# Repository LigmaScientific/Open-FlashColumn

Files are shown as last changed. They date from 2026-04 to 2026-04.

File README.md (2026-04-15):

# Open-FlashColumn
An open-source flash-column chromatography system.

Abstract

Flash column chromatography is a method used in organic synthesis research to separate and purify chemicals. Compounds are separated by being forced through silica gel with a pressurized solvent, which separates them based on polarity. The project focuses on the research and development of a flash-column chromatography column that enables users to visualize the separation of compounds in real-time using an ultraviolet lamp and fluorescent silica. The system was constructed using a combination of 3D-printed components and commercial off-the-shelf components to minimize costs. Furthermore, the apparatus is designed for easy visualization of fractions, needing only a handheld UV lamp at 254nm to visualize the absorbance of each analyte as they separate. The 3D-printed components are designed to be durable against both chemicals and UV radiation, and can be manufactured on commonly available printers using standard filaments. The flash column can resolve a wide range of analytes and works with mixtures of ethyl acetate and hexane. Separations are on par with or more efficient than traditional flash columns, and the system offers ease of use that falls somewhere between commercial flash chromatography machines and traditional flash columns. The low per-unit cost and commercial-off-the-shelf components make the system both affordable and accessible, making it well-suited for use in teaching laboratories and those on a tight budget. The project is intended to be open-source, with digital files published under a permissive license that allows others to reproduce the results and build upon the column. This ensures continued support for the project so that the system will be easily repairable.

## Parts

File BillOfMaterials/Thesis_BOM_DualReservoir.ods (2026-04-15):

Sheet: 2-Reservoir-DIY
Component | Size | QTY (build) | QTY (purchase) | Unit Price | Total Price | SKU | Link | Manufacturer | Source | Notes
SwageLok MNPT-Tube fitting | 1/8” MNPT x 1/8” tube | 9 | 9 | $5.50 | $49.50 | B-200-1-2 | https://products.swagelok.com/en/c/straights/p/B-200-1-2 | Swagelok | W&M Chem Dept. | Comes w/ Nuts and Ferrules
SwageLok Nut | 1/8” tube | 0 | 10 | $1.56 | $15.60 | B-202-1 | https://products.swagelok.com/en/c/female-nuts/p/B-202-1 | Swagelok | W&M Chem Dept. | Spares
Swagelok ferrule | 1/8” tube | 0 | 10 | $1.70 | $17.00 | B-200-SET | https://products.swagelok.com/en/c/ferrule-sets/p/B-200-SET | Swagelok | W&M Chem Dept. | Spares
Swagelok bulkhead fitting | 1/8” tube | 2 | 2 | $16.83 | $33.66 | B-200-61 | https://products.swagelok.com/en/c/straights/p/B-200-61 | Swagelok | W&M Chem Dept. | Can be substituted w/ thru-bore swagelok fitting, however tubing length for reservoir is fixed if done so
FNPT-MNPT standoff | 1/8” FNPT x 1/8” MNPT | 4 | 1 | $9.99 | $9.99 | 769018946082 | https://www.amazon.com/JSMOUID-Adapters-Extension-Connectors-Bathroom/dp/B0DXCZHD25 | JSMOUID | Amazon | 4-pack
3/8” Brass Washer | 3/8 ID, ½ OD | 2 | 2 | $0.75 | $1.50 | 1297-P |  | Hillman | ACE hardware
1/8” OD, 1/16” ID Copper tubing | 1.5” long | 1 | 1 | $6.89 | $6.89 | B07QVND41W | https://www.amazon.com/uxcell-Refrigeration-Tubing-inches-Copper/dp/B07QZVLB82/ | Restek | W&M Chem Dept. | generic tubing linked
1/8” OD, 1/16” ID PTFE tubing | 20.5” long | 1 | 1 | $20.80 | $20.80 | 193005153809 | https://www.amazon.com/dp/B07K7RRW93 | USA Sealing Inc | Amazon | 1 pack covers all the tubing, arbitrary length (for convenience); 10 feet total
1/8” OD, 1/16” ID PTFE tubing | 16” long | 2 |  |  | $0.00
1/8” OD, 1/16” ID PTFE tubing | 10.5” long | 2 |  |  | $0.00
1/8” OD, 1/16” ID PTFE tubing | 9.5” long | 2 |  |  | $0.00 |  |  |  |  | Reservoir tube, must be exact
¼” silicone tube | 36” long | 2 | 1 | $8.69 | $8.69 | B0DST875BW | https://www.amazon.com/Rebower-Silicone-Silicon-Brewing-Aquarium/dp/B0DST875BW | Rebower | Amazon | 1 pack covers all the tubing, arbitrary length (for convenience); 10 feet total
¼” silicone tube | 24” long | 1 |  |  | $0.00 |  |  |  |  | Arbitrary length
¼” tube tee-joint | ¼” tube | 1 | 1 | $4.99 | $4.99 | QL2406371TA008K1 | https://www.amazon.com/PAGOW-Fitting-Plastic-Barbed-Household/dp/B0DNYX6LYN | PAGOW | Amazon | 4-pack, only need one
Pressure gauge, 30 PSI | 1/8” MNPT | 2 | 2 | $14.15 | $28.30 | 4000K717 | https://www.mcmaster.com/4000K717/ | Ashcroft | Mcmaster
Pressure relief valve, 25 PSI | 1/8” MNPT | 2 | 2 | $11.45 | $22.90 | SRH250-18 | https://www.amazon.com/dp/B0B32RQDM5 | Conrader | Amazon | Can be substituted w/ McMaster 4772K2
Ball valve, NPT | 1/8” FNPT x 1/8” MNPT | 2 | 2 | $18.99 | $37.98 | 1zf-00425-mvn | https://www.amazon.com/dp/B0D2MTSMMZ | Beduan | Amazon | 3 used, though a fourth can be used to increase deadspace for analyte loading.
NPT tee | FNPT x 1/8” FNPT x 1/8” MNPT | 2 | 1 | $6.99 | $6.99 | SG-PFBST18-2_1 | https://www.amazon.com/dp/B0B9M4HKMT | SUNGATOR | Amazon | 2-Pack
¼” barb fitting | 1/8” MNPT | 2 | 1 | $6.99 | $6.99 | CA-125 4A-4 | https://www.amazon.com/dp/B07P962KXQ | KOOTANS | Amazon | 4-pack, only need two
Precision needle valve | 1/8” FNPT x 1/8” FNPT | 2 | 2 | $52.71 | $105.42 | 46425K11 | https://www.mcmaster.com/46425K11/ | Deltrol | McMaster | valve is directional
Viton O-ring | -123 | 2 | 1 | $9.64 | $9.64 | 9464K87 | https://www.mcmaster.com/9464K87/ |  | McMaster | 25-pack
Buna-N Gasket | 2-1/2” nominal | 2 | 2 | $2.54 | $5.08 | 4524K51 | https://www.mcmaster.com/4524K51/ |  | McMaster
Neoprene gasket | 5/16” ID, ¾” OD, 1/16” thick | 2 | 2 | $0.65 | $1.30 | 3183-D |  | Hillman | ACE hardware | can be substituted w/ buna-n or viton if needed.
Brass Bulkhead nut | 3/8-24, incl. w/ bulkhead | 2 | 0 |  | $0.00 |  |  | Hillman | W&M Chem Dept. | Included w/ bulkhead
10-32 threaded rod | 9.5” long | 2 | 1 | $2.39 | $2.39 | 98838A011 | https://www.mcmaster.com/products/98838a011/ |  | McMaster | 3’, Cut to match length of column
10-32 wing nuts | 10-32 thread | 2 | 2 | $0.69 | $1.38 | 4341-D |  | Hillman | ACE hardware
#10 washers | 10 | 4 | 4 | $0.15 | $0.60 | 8305556 |  | Hillman | ACE hardware
10-32 acorn nuts | 10-32 thread | 2 | 2 | $0.99 | $1.98 | 861-R |  | Hillman | ACE hardware | Use Blue thread; brass, can be galvanized
GL-80 bottle | GL-80 thread | 2 | 1 | $35.99 | $35.99 | 611851182250 | https://www.amazon.com/dp/B0912N5WJT | Moonetto | Amazon | 3-pack
GL-80 lid, PETG | GL-80 thread | 2 | 2 | 62.03g | 124.06g | N/A |  | DIY | DIY | 3D printed
4-port lid, PETG | 1/8” NPT (tapped), 7mm hole (bulkhead) | 2 | 2 | 37.36g | 74.72g | N/A |  | DIY | DIY | 3D printed, Solvent Sealed
PETG Endcap (Top) | 1/8” FNPT | 1 | 1 | 78.22g | 78.22g | N/A |  | DIY | DIY | 3D printed, Solvent Sealed
PETG Endcap (Bottom) | 1/8” FNPT | 1 | 1 | 75.58g | 75.58g | N/A |  | DIY | DIY | 3D printed, Solvent Sealed
PETG Mixer | 1/8” FNPT | 1 | 1 | 28.71g | 28.71g | N/A |  | DIY | DIY | 3D printed, Solvent Sealed
PETG Peak Tracker | 30.45mm ID | 1 | 1 | 8.52g | 8.52g | N/A |  | DIY | DIY | 3D printed
PETG Locking Ring | 30.45mm ID | 2 | 2 | 10.15g | 20.30g | N/A |  | DIY | DIY | 3D printed
Quartz Envelope | 200mm length, 30 mm OD, 2.5 mm wall thickness | 1 | 1 | $20.00 | $20.00 | ‎B0C2875X67 | https://www.amazon.com/dp/B0C2875X67 | Deschem Scientific Supply | Amazon | Can be substituted w/ borosilicate glass if external detector is used. Can be longer.
Polymaker PETG | 1 kg | 1 | 1 | $18.99 | $18.99 | B0FG3FHG29 | https://www.amazon.com/dp/B0FG3FHG29 | Polymaker | Amazon
Aggregate price: | $474.55 |  |  |  |  |  |  |  | W&M means I got it from the Chem Department; can be ordered w/ an account

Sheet: 2-Reservoir-PrintPurchase
Component | Size | QTY (build) | QTY (purchase) | Unit Price | Total Price | SKU | Link | Manufacturer | W&M Chem Dept. | Notes
SwageLok MNPT-Tube fitting | 1/8” MNPT x 1/8” tube | 9 | 9 | $5.50 | $49.50 | B-200-1-2 | https://products.swagelok.com/en/c/straights/p/B-200-1-2 | Swagelok | W&M Chem Dept. | Comes w/ Nuts and Ferrules
SwageLok Nut | 1/8” tube | 13 | 10 | $1.56 | $15.60 | B-202-1 | https://products.swagelok.com/en/c/female-nuts/p/B-202-1 | Swagelok | W&M Chem Dept. | Spares
Swagelok ferrule | 1/8” tube | 13 | 10 | $1.70 | $17.00 | B-200-SET | https://products.swagelok.com/en/c/ferrule-sets/p/B-200-SET | Swagelok | W&M Chem Dept. | Spares
Swagelok bulkhead fitting | 1/8” tube | 2 | 2 | $16.83 | $33.66 | B-200-61 | https://products.swagelok.com/en/c/straights/p/B-200-61 | Swagelok | W&M Chem Dept. | Can be substituted w/ thru-bore swagelok fitting, however tubing length for reservoir is fixed if done so
FNPT-MNPT standoff | 1/8” FNPT x 1/8” MNPT | 4 | 1 | $9.99 | $9.99 | 769018946082 | https://www.amazon.com/JSMOUID-Adapters-Extension-Connectors-Bathroom/dp/B0DXCZHD25 | JSMOUID | Amazon | 4-pack
3/8” Brass Washer | 3/8 ID, ½ OD | 2 | 2 | $0.75 | $1.50 | 1297-P |  | Hillman | ACE hardware
1/8” OD, 1/16” ID Copper tubing | 1.5” long | 1 | 1 | $6.89 | $6.89 | B07QVND41W | https://www.amazon.com/uxcell-Refrigeration-Tubing-inches-Copper/dp/B07QZVLB82/ | Restek | W&M Chem Dept. | generic tubing linked
1/8” OD, 1/16” ID PTFE tubing | 20.5” long | 1 | 1 | $20.80 | $20.80 | 193005153809 | https://www.amazon.com/dp/B07K7RRW93 | USA Sealing Inc | Amazon | 1 pack covers all the tubing, arbitrary length (for convenience); 10 feet total
1/8” OD, 1/16” ID PTFE tubing | 16” long | 2 |  |  | $0.00
1/8” OD, 1/16” ID PTFE tubing | 10.5” long | 2 |  |  | $0.00
1/8” OD, 1/16” ID PTFE tubing | 9.5” long | 2 |  |  | $0.00 |  |  |  |  | Reservoir tube, must be exact
¼” silicone tube | 36” long | 2 | 1 | $8.69 | $8.69 | B0DST875BW | https://www.amazon.com/Rebower-Silicone-Silicon-Brewing-Aquarium/dp/B0DST875BW | Rebower | Amazon | 1 pack covers all the tubing, arbitrary length (for convenience); 10 feet total
¼” silicone tube | 24” long | 1 |  |  | $0.00 |  |  |  |  | Arbitrary length
¼” tube tee-joint | ¼” tube | 1 | 1 | $4.99 | $4.99 | QL2406371TA008K1 | https://www.amazon.com/PAGOW-Fitting-Plastic-Barbed-Household/dp/B0DNYX6LYN | PAGOW | Amazon | 4-pack, only need one
Pressure gauge, 30 PSI | 1/8” MNPT | 2 | 2 | $14.15 | $28.30 | 4000K717 | https://www.mcmaster.com/4000K717/ | Ashcroft | Mcmaster
Pressure relief valve, 25 PSI | 1/8” MNPT | 2 | 2 | $11.45 | $22.90 | SRH250-18 | https://www.amazon.com/dp/B0B32RQDM5 | Conrader | Amazon | Can be substituted w/ McMaster 4772K2
Ball valve, NPT | 1/8” FNPT x 1/8” MNPT | 2 | 2 | $18.99 | $37.98 | 1zf-00425-mvn | https://www.amazon.com/dp/B0D2MTSMMZ | Beduan | Amazon | 3 used, though a fourth can be used to increase deadspace for analyte loading.
NPT tee | FNPT x 1/8” FNPT x 1/8” MNPT | 2 | 1 | $6.99 | $6.99 | SG-PFBST18-2_1 | https://www.amazon.com/dp/B0B9M4HKMT | SUNGATOR | Amazon | 2-Pack
¼” barb fitting | 1/8” MNPT | 2 | 1 | $6.99 | $6.99 | CA-125 4A-4 | https://www.amazon.com/dp/B07P962KXQ | KOOTANS | Amazon | 4-pack, only need two
Precision needle valve | 1/8” FNPT x 1/8” FNPT | 2 | 2 | $52.71 | $105.42 | 46425K11 | https://www.mcmaster.com/46425K11/ | Deltrol | McMaster | valve is directional
Viton O-ring | -123 | 2 | 1 | $9.64 | $9.64 | 9464K87 | https://www.mcmaster.com/9464K87/ |  | McMaster | 25-pack
Buna-N Gasket | 2-1/2” nominal | 2 | 2 | $2.54 | $5.08 | 4524K51 | https://www.mcmaster.com/4524K51/ |  | McMaster
Neoprene gasket | 5/16” ID, ¾” OD, 1/16” thick | 2 | 2 | $0.65 | $1.30 | 3183-D |  | Hillman | ACE hardware | can be substituted w/ buna-n or viton if needed.
Brass Bulkhead nut | 3/8-24, incl. w/ bulkhead | 2 | 0 |  | $0.00 |  |  | Hillman | W&M Chem Dept. | Included w/ bulkhead
10-32 threaded rod | 9.5” long | 2 | 1 | $2.39 | $2.39 | 98838A011 | https://www.mcmaster.com/products/98838a011/ |  | McMaster | 3’, Cut to match length of column
10-32 wing nuts | 10-32 thread | 2 | 2 | $0.69 | $1.38 | 4341-D |  | Hillman | ACE hardware
#10 washers | 10 | 4 | 4 | $0.15 | $0.60 | 8305556 |  | Hillman | ACE hardware
10-32 acorn nuts | 10-32 thread | 2 | 2 | $0.99 | $1.98 | 861-R |  | Hillman | ACE hardware | Use Blue thread; brass, can be galvanized
GL-80 bottle | GL-80 thread | 2 | 1 | $35.99 | $35.99 | 611851182250 | https://www.amazon.com/dp/B0912N5WJT | Moonetto | Amazon | 3-pack
GL-80 lid, PETG | GL-80 thread | 2 | 2 | $10.70 | $21.40 | N/A |  | Ligma Scientific | Ligma Scientific | For Print Purchase, prices may vary from vendor to vendor. Ligma Scientific charges $0.05/g plus $1.00 per print hour.
4-port lid, PETG | 1/8” NPT (tapped), 7mm hole (bulkhead) | 2 | 2 | $5.49 | $10.98 | N/A |  | Ligma Scientific | Ligma Scientific
PETG Endcap (Top) | 1/8” FNPT | 1 | 1 | $10.56 | $10.56 | N/A |  | Ligma Scientific | Ligma Scientific
PETG Endcap (Bottom) | 1/8” FNPT | 1 | 1 | $11.32 | $11.32 | N/A |  | Ligma Scientific | Ligma Scientific
PETG Mixer | 1/8” FNPT | 1 | 1 | $6.63 | $6.63 | N/A |  | Ligma Scientific | Ligma Scientific
PETG Peak Tracker | 30.45mm ID | 1 | 1 | $1.61 | $1.61 |  |  | Ligma Scientific | Ligma Scientific
PETG Locking Ring | 30.45mm ID | 2 | 2 | $1.82 | $3.64 |  |  | Ligma Scientific | Ligma Scientific
Quartz Envelope | 200mm length, 30 mm OD, 2.5 mm wall thickness | 1 | 1 | $20.00 | $20.00 | ‎B0C2875X67 | https://www.amazon.com/dp/B0C2875X67 | Deschem Scientific Supply | Amazon | Can be substituted w/ borosilicate glass if external detector is used. Can be longer.
Aggregate price: | $521.70

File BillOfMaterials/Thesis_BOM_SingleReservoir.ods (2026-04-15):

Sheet: 1-Reservoir-DIY
Component | Size | QTY (build) | QTY (purchase) | Unit Price | Total Price | SKU | Link | Manufacturer | Source | Notes
SwageLok MNPT-Tube fitting | 1/8” MNPT x 1/8” tube | 6 | 6 | $5.50 | $33.00 | B-200-1-2 | https://products.swagelok.com/en/c/straights/p/B-200-1-2 | Swagelok | W&M Chem Dept. | Comes w/ Nuts and Ferrules
SwageLok Nut | 1/8” tube | 0 | 10 | $1.56 | $15.60 | B-202-1 | https://products.swagelok.com/en/c/female-nuts/p/B-202-1 | Swagelok | W&M Chem Dept. | Spares
Swagelok ferrule | 1/8” tube | 0 | 10 | $1.70 | $17.00 | B-200-SET | https://products.swagelok.com/en/c/ferrule-sets/p/B-200-SET | Swagelok | W&M Chem Dept. | Spares
Swagelok bulkhead fitting | 1/8” tube | 1 | 1 | $16.83 | $16.83 | B-200-61 | https://products.swagelok.com/en/c/straights/p/B-200-61 | Swagelok | W&M Chem Dept. | Can be substituted w/ thru-bore swagelok fitting, however tubing length for reservoir is fixed if done so
FNPT-MNPT standoff | 1/8” FNPT x 1/8” MNPT | 2 | 1 | $9.99 | $9.99 | 769018946082 | https://www.amazon.com/JSMOUID-Adapters-Extension-Connectors-Bathroom/dp/B0DXCZHD25 | JSMOUID | Amazon | 4-pack
3/8” Brass Washer | 3/8 ID, ½ OD | 1 | 1 | $0.75 | $0.75 | 1297-P |  | Hillman | ACE hardware
1/8” OD, 1/16” ID Copper tubing | 1.5” long | 1 | 1 | $6.89 | $6.89 | B07QVND41W | https://www.amazon.com/uxcell-Refrigeration-Tubing-inches-Copper/dp/B07QZVLB82/ | Restek | W&M Chem Dept. | generic tubing linked
1/8” OD, 1/16” ID PTFE tubing | 20.5” long | 1 | 1 | $20.80 | $20.80 | 193005153809 | https://www.amazon.com/dp/B07K7RRW93 | USA Sealing Inc | Amazon | 1 pack covers all the tubing, arbitrary length (for convenience); 10 feet total
1/8” OD, 1/16” ID PTFE tubing | 16” long | 0 |  |  | $0.00
1/8” OD, 1/16” ID PTFE tubing | 10.5” long | 0 |  |  | $0.00
1/8” OD, 1/16” ID PTFE tubing | 9.5” long | 1 |  |  | $0.00 |  |  |  |  | Reservoir tube, must be exact
¼” silicone tube | 36” long | 1 | 1 | $8.69 | $8.69 | B0DST875BW | https://www.amazon.com/Rebower-Silicone-Silicon-Brewing-Aquarium/dp/B0DST875BW | Rebower | Amazon | 1 pack covers all the tubing, arbitrary length (for convenience); 10 feet total
¼” silicone tube | 24” long | 0 |  |  | $0.00 |  |  |  |  | Arbitrary length
¼” tube tee-joint | ¼” tube | 1 | 1 | $4.99 | $4.99 | QL2406371TA008K1 | https://www.amazon.com/PAGOW-Fitting-Plastic-Barbed-Household/dp/B0DNYX6LYN | PAGOW | Amazon | 4-pack, only need one
Pressure gauge, 30 PSI | 1/8” MNPT | 1 | 1 | $14.15 | $14.15 | 4000K717 | https://www.mcmaster.com/4000K717/ | Ashcroft | Mcmaster
Pressure relief valve, 25 PSI | 1/8” MNPT | 1 | 1 | $11.45 | $11.45 | SRH250-18 | https://www.amazon.com/dp/B0B32RQDM5 | Conrader | Amazon | Can be substituted w/ McMaster 4772K2
Ball valve, NPT | 1/8” FNPT x 1/8” MNPT | 2 | 1 | $18.99 | $18.99 | 1zf-00425-mvn | https://www.amazon.com/dp/B0D2MTSMMZ | Beduan | Amazon | 2 used, though a third can be used to increase deadspace for analyte loading.
 |  |  |  |  | $0.00
NPT tee | FNPT x 1/8” FNPT x 1/8” MNPT | 2 | 1 | $6.99 | $6.99 | SG-PFBST18-2_1 | https://www.amazon.com/dp/B0B9M4HKMT | SUNGATOR | Amazon | 2-Pack
¼” barb fitting | 1/8” MNPT | 1 | 1 | $6.99 | $6.99 | CA-125 4A-4 | https://www.amazon.com/dp/B07P962KXQ | KOOTANS | Amazon | 4-pack, only need two
Precision needle valve | 1/8” FNPT x 1/8” FNPT | 1 | 1 | $52.71 | $52.71 | 46425K11 | https://www.mcmaster.com/46425K11/ | Deltrol | McMaster | valve is directional
Viton O-ring | -123 | 1 | 1 | $9.64 | $9.64 | 9464K87 | https://www.mcmaster.com/9464K87/ |  | McMaster | 25-pack
Buna-N Gasket | 2-1/2” nominal | 1 | 1 | $2.54 | $2.54 | 4524K51 | https://www.mcmaster.com/4524K51/ |  | McMaster
 |  |  |  |  | $0.00
Neoprene gasket | 5/16” ID, ¾” OD, 1/16” thick | 1 | 1 | $0.65 | $0.65 | 3183-D |  | Hillman | ACE hardware | can be substituted w/ buna-n or viton if needed.
Brass Bulkhead nut | 3/8-24, incl. w/ bulkhead | 1 | 0 |  | $0.00 |  |  | Hillman | W&M Chem Dept. | Included w/ bulkhead
10-32 threaded rod | 9.5” long | 2 | 1 | $2.39 | $2.39 | 98838A011 | https://www.mcmaster.com/products/98838a011/ |  | McMaster | 3’, Cut to match length of column
10-32 wing nuts | 10-32 thread | 2 | 2 | $0.69 | $1.38 | 4341-D |  | Hillman | ACE hardware
#10 washers | 10 | 4 | 4 | $0.15 | $0.60 | 8305556 |  | Hillman | ACE hardware
10-32 acorn nuts | 10-32 thread | 2 | 2 | $0.99 | $1.98 | 861-R |  | Hillman | ACE hardware | Use Blue thread; brass, can be galvanized
GL-80 bottle | GL-80 thread | 2 | 1 | $35.99 | $35.99 | 611851182250 | https://www.amazon.com/dp/B0912N5WJT | Moonetto | Amazon | 3-pack
GL-80 lid, PETG | GL-80 thread | 1 | 1 | 62.03g | 62.03g | N/A |  | Ligma Scientific | Ligma Scientific | 3D printed
4-port lid, PETG | 1/8” NPT (tapped), 7mm hole (bulkhead) | 1 | 1 | 37.36g | 37.36g | N/A |  | Ligma Scientific | Ligma Scientific | 3D printed, Solvent Sealed
PETG Endcap (Top) | 1/8” FNPT | 1 | 1 | 78.22g | 78.22g | N/A |  | Ligma Scientific | Ligma Scientific | 3D printed, Solvent Sealed
PETG Endcap (Bottom) | 1/8” FNPT | 1 | 1 | 75.58g | 75.58g | N/A |  | Ligma Scientific | Ligma Scientific | 3D printed, Solvent Sealed
PETG Peak Tracker | 30.45mm ID | 1 | 1 | 8.52g | 8.52g | N/A |  | Ligma Scientific | Ligma Scientific | 3D printed
PETG Locking Ring | 30.45mm ID | 2 | 2 | 10.15g | 10.15g | N/A |  | Ligma Scientific | Ligma Scientific | 3D printed
Quartz Envelope | 200mm length, 30 mm OD, 2.5 mm wall thickness | 1 | 1 | $20.00 | $20.00 | ‎B0C2875X67 | https://www.amazon.com/dp/B0C2875X67 | Deschem Scientific Supply | Amazon | Can be substituted w/ borosilicate glass if external detector is used. Can be longer.
Polymaker PETG | 1 kg | 1 | 1 | $18.99 | $18.99 | B0FG3FHG29 | https://www.amazon.com/dp/B0FG3FHG29 | Polymaker | Amazon | only purchase if printing
Aggregate price: | $339.98 |  |  |  |  |  |  |  | W&M means I got it from the Chem Department; can be ordered w/ an account

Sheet: 1-Reservoir-PrintPurchase
Component | Size | QTY (build) | QTY (purchase) | Unit Price | Total Price | SKU | Link | Manufacturer | Source | Notes
SwageLok MNPT-Tube fitting | 1/8” MNPT x 1/8” tube | 6 | 6 | $5.50 | $33.00 | B-200-1-2 | https://products.swagelok.com/en/c/straights/p/B-200-1-2 | Swagelok | W&M Chem Dept. | Comes w/ Nuts and Ferrules
SwageLok Nut | 1/8” tube | 13 | 10 | $1.56 | $20.28 | B-202-1 | https://products.swagelok.com/en/c/female-nuts/p/B-202-1 | Swagelok | W&M Chem Dept. | Spares
Swagelok ferrule | 1/8” tube | 13 | 10 | $1.70 | $22.10 | B-200-SET | https://products.swagelok.com/en/c/ferrule-sets/p/B-200-SET | Swagelok | W&M Chem Dept. | Spares
Swagelok bulkhead fitting | 1/8” tube | 1 | 1 | $16.83 | $16.83 | B-200-61 | https://products.swagelok.com/en/c/straights/p/B-200-61 | Swagelok | W&M Chem Dept. | Can be substituted w/ thru-bore swagelok fitting, however tubing length for reservoir is fixed if done so
FNPT-MNPT standoff | 1/8” FNPT x 1/8” MNPT | 2 | 1 | $9.99 | $9.99 | 769018946082 | https://www.amazon.com/JSMOUID-Adapters-Extension-Connectors-Bathroom/dp/B0DXCZHD25 | JSMOUID | Amazon | 4-pack
3/8” Brass Washer | 3/8 ID, ½ OD | 1 | 1 | $0.75 | $0.75 | 1297-P |  | Hillman | ACE hardware
1/8” OD, 1/16” ID Copper tubing | 1.5” long | 1 | 1 | $6.89 | $6.89 | B07QVND41W | https://www.amazon.com/uxcell-Refrigeration-Tubing-inches-Copper/dp/B07QZVLB82/ | Restek | W&M Chem Dept. | generic tubing linked
1/8” OD, 1/16” ID PTFE tubing | 20.5” long | 1 | 1 | $20.80 | $20.80 | 193005153809 | https://www.amazon.com/dp/B07K7RRW93 | USA Sealing Inc | Amazon | 1 pack covers all the tubing, arbitrary length (for convenience); 10 feet total
1/8” OD, 1/16” ID PTFE tubing | 16” long | 0
1/8” OD, 1/16” ID PTFE tubing | 10.5” long | 0
1/8” OD, 1/16” ID PTFE tubing | 9.5” long | 1 |  |  |  |  |  |  |  | Reservoir tube, must be exact
¼” silicone tube | 36” long | 1 | 1 | $8.69 | $8.69 | B0DST875BW | https://www.amazon.com/Rebower-Silicone-Silicon-Brewing-Aquarium/dp/B0DST875BW | Rebower | Amazon | 1 pack covers all the tubing, arbitrary length (for convenience); 10 feet total
¼” silicone tube | 24” long | 0 |  |  |  |  |  |  |  | Arbitrary length
¼” tube tee-joint | ¼” tube | 1 | 1 | $4.99 | $4.99 | QL2406371TA008K1 | https://www.amazon.com/PAGOW-Fitting-Plastic-Barbed-Household/dp/B0DNYX6LYN | PAGOW | Amazon | 4-pack, only need one
Pressure gauge, 30 PSI | 1/8” MNPT | 1 | 1 | $14.15 | $14.15 | 4000K717 | https://www.mcmaster.com/4000K717/ | Ashcroft | Mcmaster
Pressure relief valve, 25 PSI | 1/8” MNPT | 1 | 1 | $11.45 | $11.45 | SRH250-18 | https://www.amazon.com/dp/B0B32RQDM5 | Conrader | Amazon | Can be substituted w/ McMaster 4772K2
Ball valve, NPT | 1/8” FNPT x 1/8” MNPT | 2 | 1 | $18.99 | $18.99 | 1zf-00425-mvn | https://www.amazon.com/dp/B0D2MTSMMZ | Beduan | Amazon | 2 used, though a third can be used to increase deadspace for analyte loading.
NPT tee | FNPT x 1/8” FNPT x 1/8” MNPT | 2 | 1 | $6.99 | $6.99 | SG-PFBST18-2_1 | https://www.amazon.com/dp/B0B9M4HKMT | SUNGATOR | Amazon | 2-Pack
¼” barb fitting | 1/8” MNPT | 1 | 1 | $6.99 | $6.99 | CA-125 4A-4 | https://www.amazon.com/dp/B07P962KXQ | KOOTANS | Amazon | 4-pack, only need two
Precision needle valve | 1/8” FNPT x 1/8” FNPT | 1 | 1 | $52.71 | $52.71 | 46425K11 | https://www.mcmaster.com/46425K11/ | Deltrol | McMaster | valve is directional
Viton O-ring | -123 | 1 | 1 | $9.64 | $9.64 | 9464K87 | https://www.mcmaster.com/9464K87/ |  | McMaster | 25-pack
Buna-N Gasket | 2-1/2” nominal | 1 | 1 | $2.54 | $2.54 | 4524K51 | https://www.mcmaster.com/4524K51/ |  | McMaster
Neoprene gasket | 5/16” ID, ¾” OD, 1/16” thick | 1 | 1 | $0.65 | $0.65 | 3183-D |  | Hillman | ACE hardware | can be substituted w/ buna-n or viton if needed.
Brass Bulkhead nut | 3/8-24, incl. w/ bulkhead | 1 | 0 |  | $0.00 |  |  | Hillman | W&M Chem Dept. | Included w/ bulkhead
10-32 threaded rod | 9.5” long | 2 | 1 | $2.39 | $2.39 | 98838A011 | https://www.mcmaster.com/products/98838a011/ |  | McMaster | 3’, Cut to match length of column
10-32 wing nuts | 10-32 thread | 2 | 2 | $0.69 | $1.38 | 4341-D |  | Hillman | ACE hardware
#10 washers | 10 | 4 | 4 | $0.15 | $0.60 | 8305556 |  | Hillman | ACE hardware
10-32 acorn nuts | 10-32 thread | 2 | 2 | $0.99 | $1.98 | 861-R |  | Hillman | ACE hardware | Use Blue thread; brass, can be galvanized
GL-80 bottle | GL-80 thread | 2 | 1 | $35.99 | $35.99 | 611851182250 | https://www.amazon.com/dp/B0912N5WJT | Moonetto | Amazon | 3-pack
GL-80 lid, PETG | GL-80 thread | 1 | 1 | $10.70 | $10.70 | N/A |  | Ligma Scientific | Ligma Scientific | For Print Purchase, prices may vary from vendor to vendor. Ligma Scientific charges $0.05/g plus $1.00 per print hour.
4-port lid, PETG | 1/8” NPT (tapped), 7mm hole (bulkhead) | 1 | 1 | $5.49 | $5.49 | N/A |  | Ligma Scientific | Ligma Scientific
PETG Endcap (Top) | 1/8” FNPT | 1 | 1 | $10.56 | $10.56 | N/A |  | Ligma Scientific | Ligma Scientific
PETG Endcap (Bottom) | 1/8” FNPT | 1 | 1 | $11.32 | $11.32 | N/A |  | Ligma Scientific | Ligma Scientific
PETG Peak Tracker | 30.45mm ID | 1 | 1 | $1.61 | $1.61 |  |  | Ligma Scientific | Ligma Scientific
PETG Locking Ring | 30.45mm ID | 2 | 2 | $1.82 | $3.64 |  |  | Ligma Scientific | Ligma Scientific
Quartz Envelope | 200mm length, 30 mm OD, 2.5 mm wall thickness | 1 | 1 | $20.00 | $20.00 | ‎B0C2875X67 | https://www.amazon.com/dp/B0C2875X67 | Deschem Scientific Supply | Amazon | Can be substituted w/ borosilicate glass if external detector is used. Can be longer.
Aggregate price: | $374.09 |  |  |  |  |  |  |  | W&M means I got it from the Chem Department; can be ordered w/ an account

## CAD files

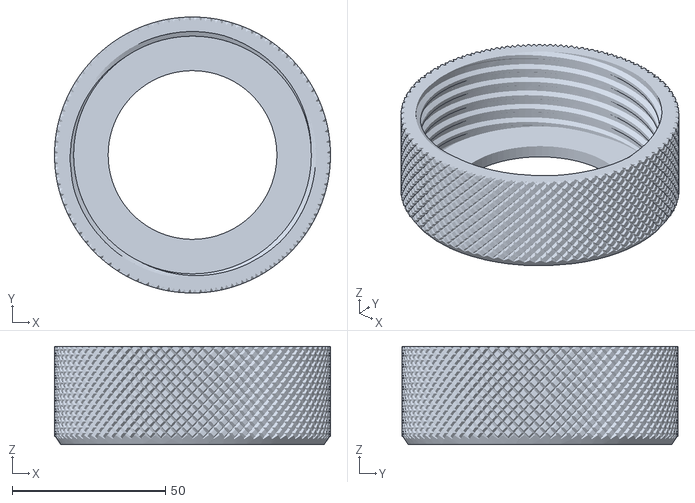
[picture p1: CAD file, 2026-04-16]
ReleaseFiles/GL-80lid-v3.stl
90.0 x 90.0 x 32.0

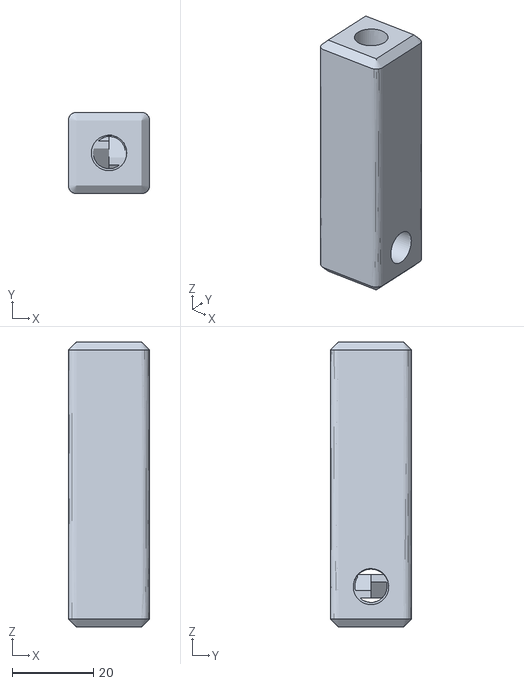
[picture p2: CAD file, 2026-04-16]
ReleaseFiles/Eluent_Mixer.stl
20.0 x 20.0 x 70.0

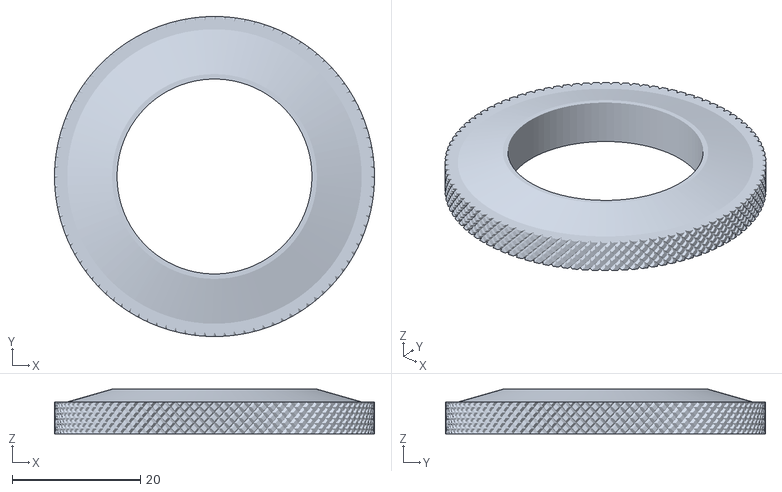
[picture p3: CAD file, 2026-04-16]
ReleaseFiles/Peak_Tracker.stl
50.0 x 50.0 x 7.00

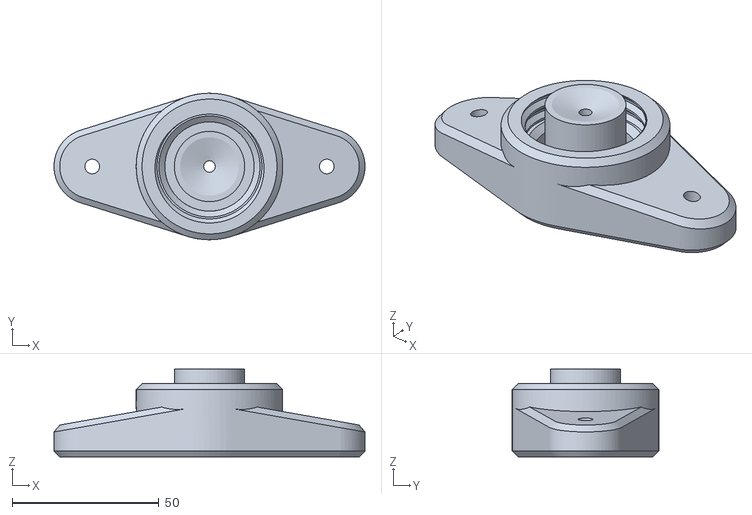
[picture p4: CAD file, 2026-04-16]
ReleaseFiles/Lower_Endcap_v5.stl
106.1 x 50.0 x 30.0

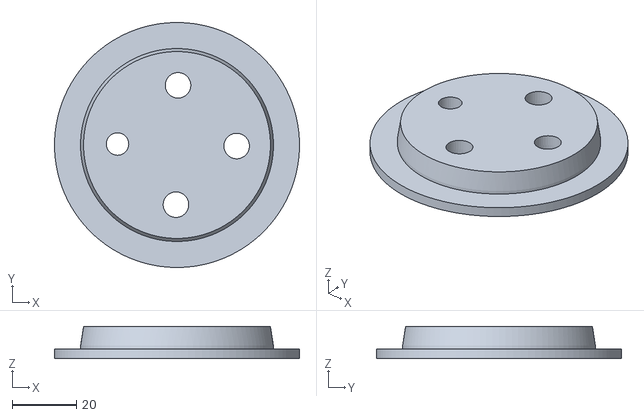
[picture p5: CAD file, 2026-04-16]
ReleaseFiles/4-portcap_v8.stl
76.2 x 76.2 x 10.0

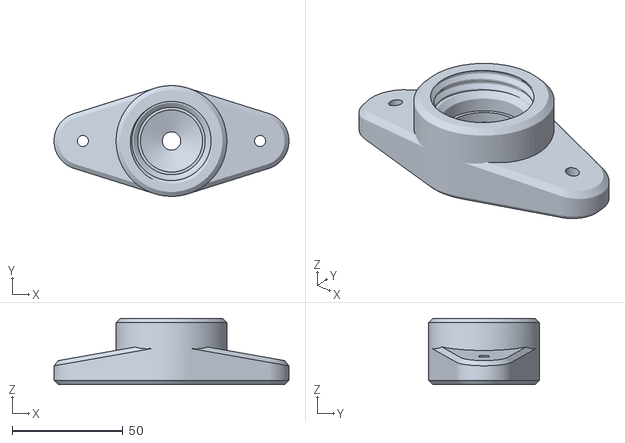
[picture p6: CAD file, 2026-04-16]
ReleaseFiles/Upper_Endcap_v4.stl
106.1 x 50.0 x 30.0

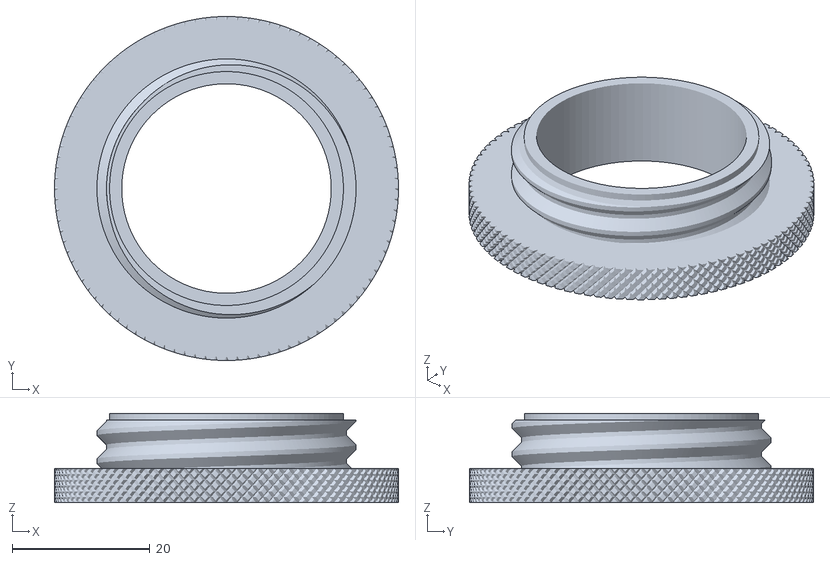
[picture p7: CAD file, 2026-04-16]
ReleaseFiles/Sealing_NutV8.stl
50.0 x 50.0 x 13.0
